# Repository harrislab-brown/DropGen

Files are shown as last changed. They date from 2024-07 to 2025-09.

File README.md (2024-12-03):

## Welcome to DropGen! A droplet on demand generator for research applications developed in the Harris Lab at Brown University

<p align="center">
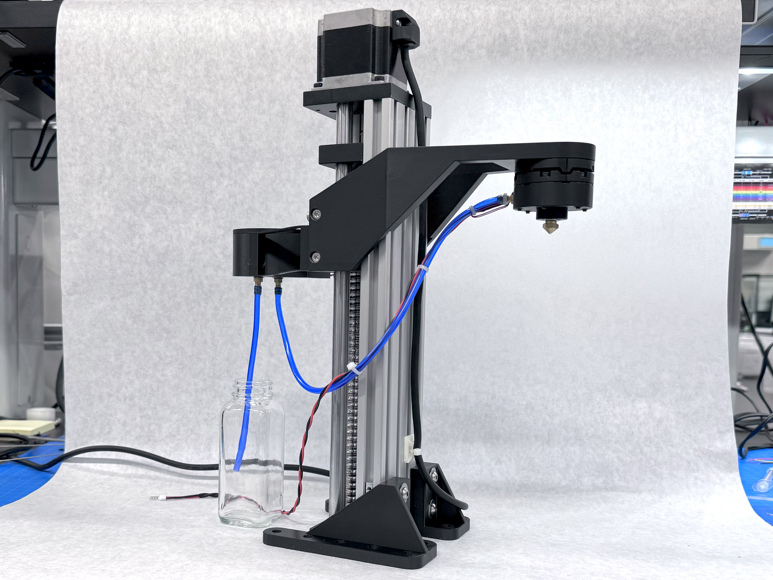
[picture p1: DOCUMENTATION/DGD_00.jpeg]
  
</p>

DropGen uses a fluid reservoir and a piezoelectric buzzer to precisely and repeatably dispense small droplets on demand. 
This new version of the Harris Lab DropGen is designed to be 3D printed using filament based FDM printers. Harris Lab has developed a custom printed circuit board to make assembly and use of DropGen as easy as possible, including adding the ability to control the height of DropGen with a commonly available stepper motor driven linear actuator. 

### WIKI:
Complete build documentation and user guide for DropGen can be found under the [Wiki](https://github.com/harrislab-brown/Filament_DropGen/wiki) tab of this repository.

### CAD: 
The CAD directory contains design files for the droplet generator 3D printed parts and the custom PCB. 
Cad files are available as a .f3z Fusion360 archive file, as well as program agnostic .step files for modification in parametric cad software. All parts that require 3D printing are also available in .stl format which can be used with all modern 3D printing slicers. 

The DropGenPCB directory contains project files for the printed circuit board. The PCB was designed using KiCad 8. Production files ready to send to JLCPCB are available here as well (see wiki for details). 

### CODE: 
DropGen is controlled by a web based GUI running on an ESP32-S3 development board. The wiki contains instructions on how to set up the environment required to flash the ESP32 firmware. 

### Documentation: 
This directory contains image and video assets used in the wiki. 

### Credit: 
If you use or adapt the device for academic publication, please cite this repository as well as the preceding works:
* N. Ionkin and D. M. Harris.  Note: A versatile 3D-printed droplet-on-demand generator. Review of Scientific Instruments. 2018; 89 (11) : 116103. [doi.org/10.1063/1.5054400](doi.org/10.1063/1.5054400)
* D. M. Harris, T. Liu and J. W. M. Bush. A low-cost, precise piezoelectric droplet-on-demand generator. Experiments in Fluids. 2015; 56 (4). [dx.doi.org/10.1007/s00348-015-1950-6](dx.doi.org/10.1007/s00348-015-1950-6)

Happy building!

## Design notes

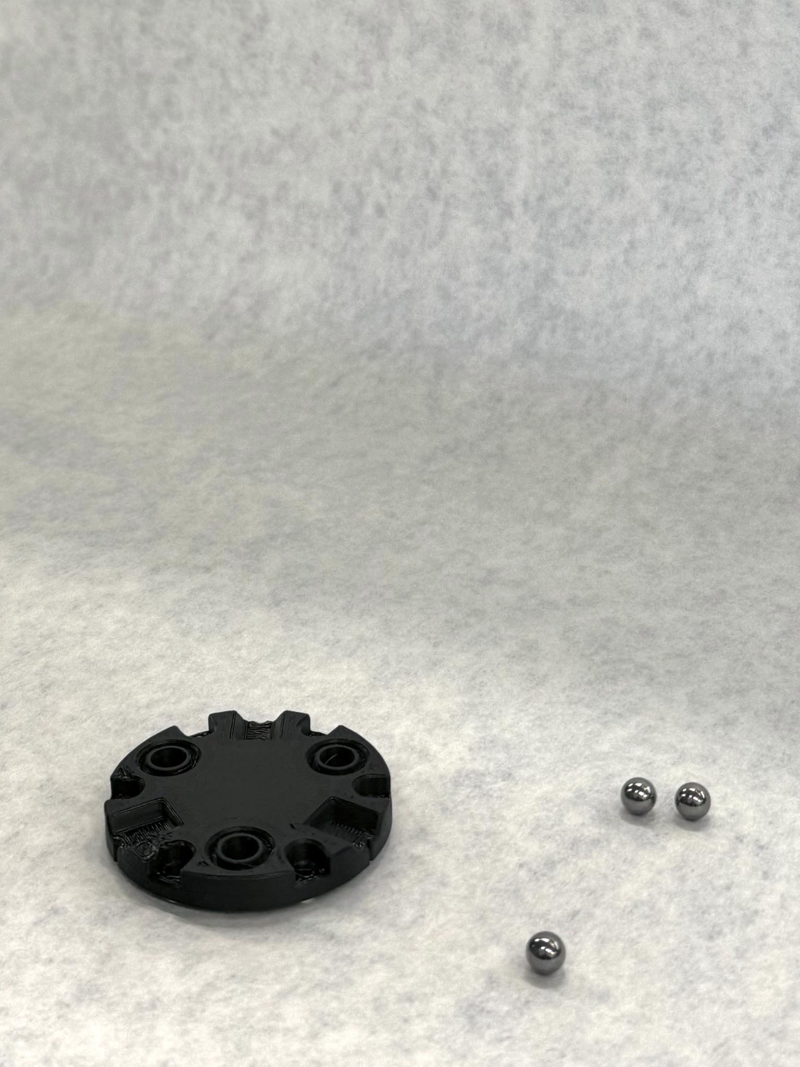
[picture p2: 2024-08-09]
DOCUMENTATION/DGD_15.jpg

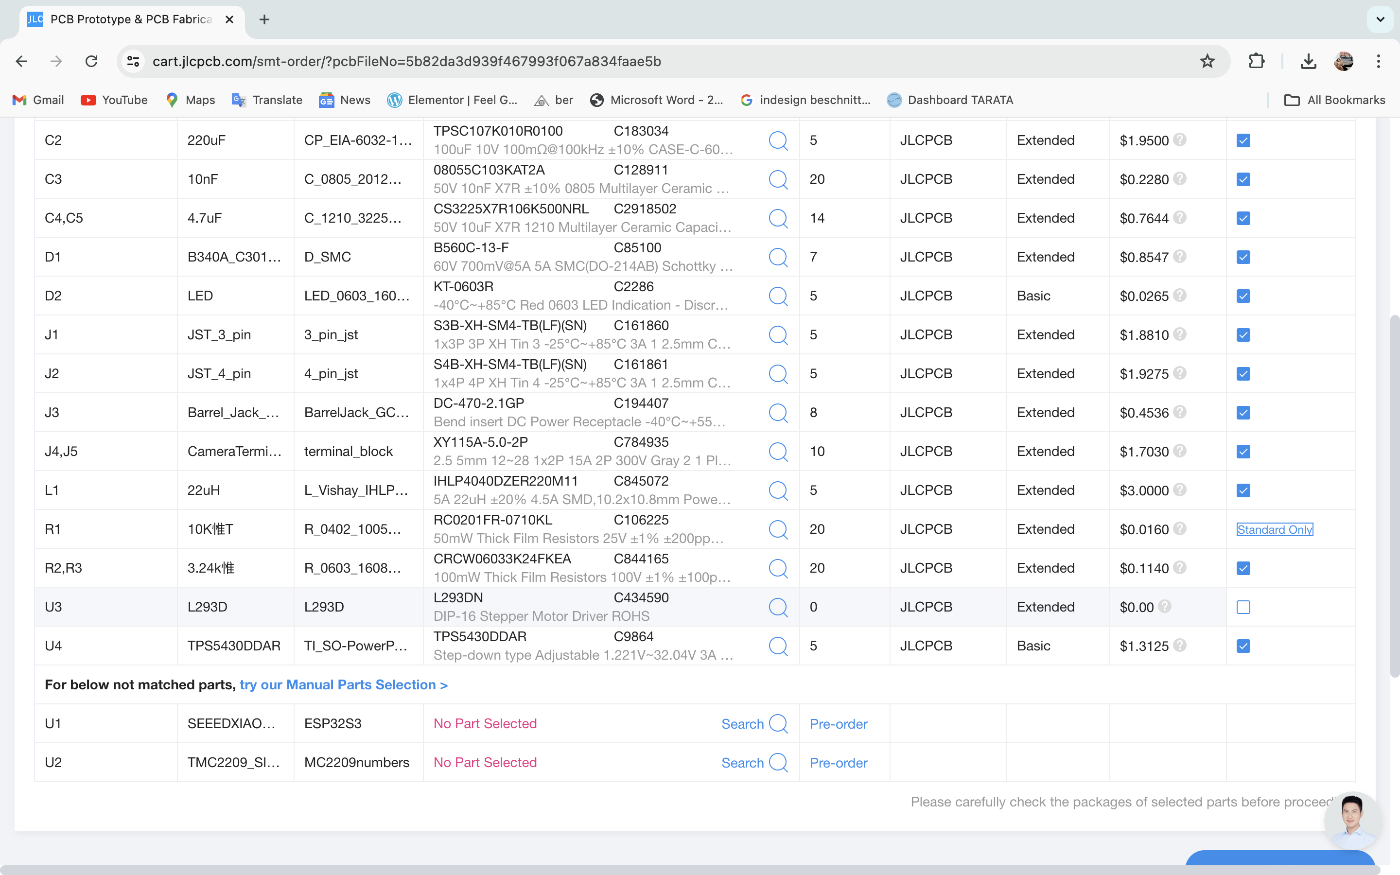
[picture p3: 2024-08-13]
DOCUMENTATION/DGD_83.png

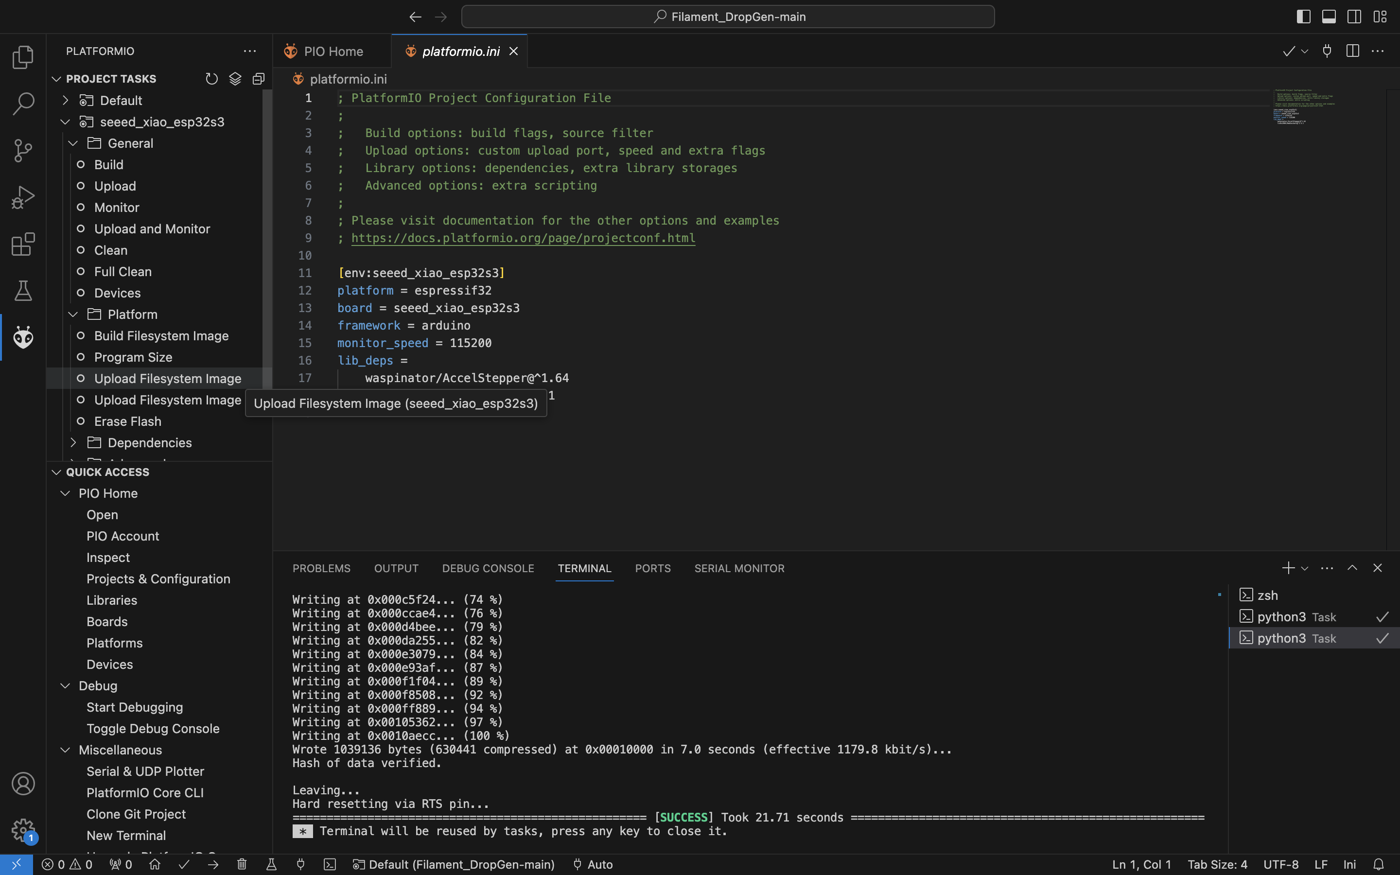
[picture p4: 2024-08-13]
DOCUMENTATION/DGD_91.png

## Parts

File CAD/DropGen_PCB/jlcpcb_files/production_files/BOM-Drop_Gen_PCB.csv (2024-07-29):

Comment | Designator | Footprint | LCSC
10KΩ T | R1 | Resistor_SMD:R_0402_1005Metric | C258091
10nF | C3 | C_0805_2012Metric | C128911
JST_3_pin | J1 | 3_pin_jst | C161860
JST_4_pin | J2 | 4_pin_jst | C161861
220uF | C2 | CP_EIA-6032-15_Kemet-U | C183034
Barrel_Jack_Switch | J3 | BarrelJack_GCT_DCJ200-10-A_Horizontal | C194407
LED | D2 | LED_0603_1608Metric | C2286
4.7uF | C4,C5 | C_1210_3225Metric | C2918502
L293D | U3 | L293D | C434590
100uF | C1 | C_Elec_6.3x7.7 | C72478
Camera Terminal Block | J4,J5 | terminal_block | C784935
3.24kΩ | R2,R3 | R_0603_1608Metric | C844165
22uH | L1 | L_Vishay_IHLP-4040 | C845072
B340A_C3018525 | D1 | D_SMC | C85100
TPS5430DDAR | U4 | TI_SO-PowerPAD-8_ThermalVias | C9864
SEEED XIAO ESP32S3 | U1 | ESP32S3
TMC2209_SILENTSTEPSTICK | U2 | MC2209 numbers

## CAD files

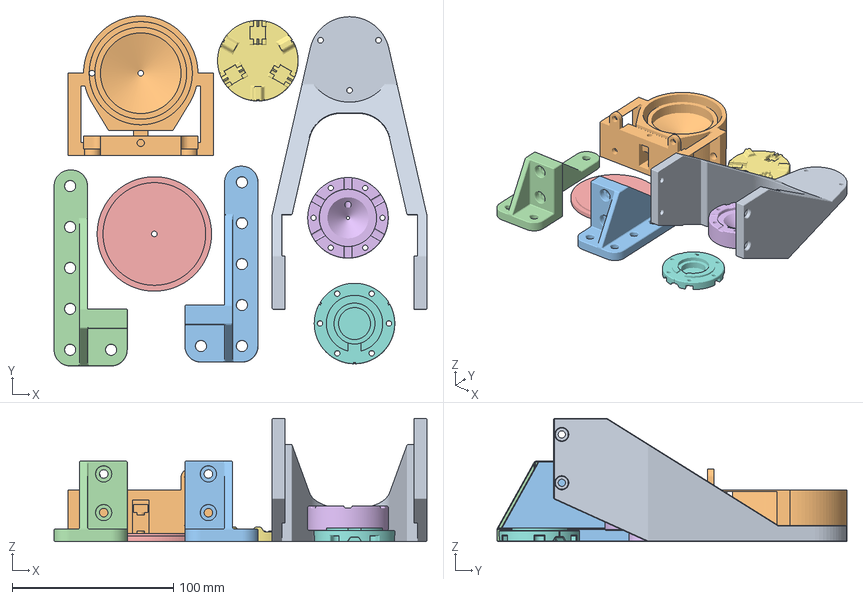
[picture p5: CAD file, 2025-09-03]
CAD/3D_Print_Files/dropgen_full_print_BambuStudio.3mf
231.3 x 217.1 x 76.5 mm
dropgen mount bracket.stl
reservoir.stl
actuator support right.stl
actuator support left.stl
reservoir lid.stl
dropgen lower print.stl
dropgen mount print.stl
dropgen upper print.stl

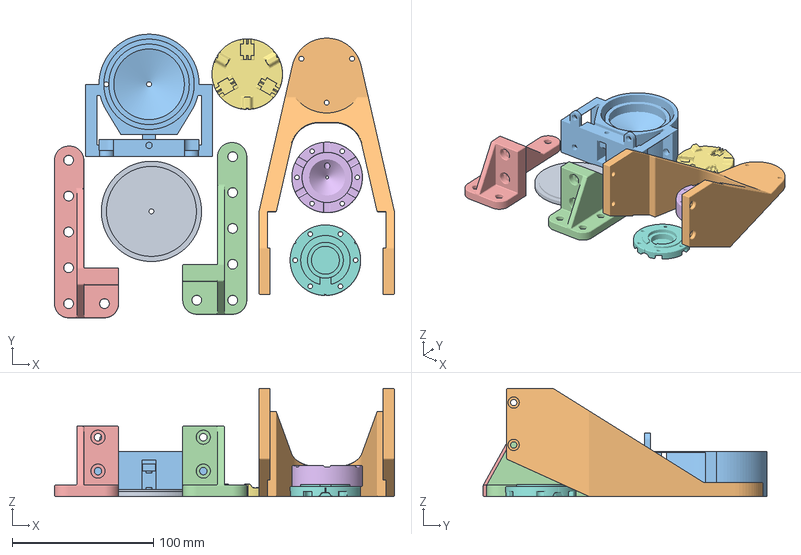
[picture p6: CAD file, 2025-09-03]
CAD/3D_Print_Files/dropgen_full_print_PrusaSlicer.3mf
240.8 x 200.9 x 76.5 mm
dropgen_print_1
dropgen_print_2
dropgen_print_3
dropgen_print_4
dropgen_print_7
dropgen lower print.stl
dropgen mount print.stl
dropgen upper print.stl

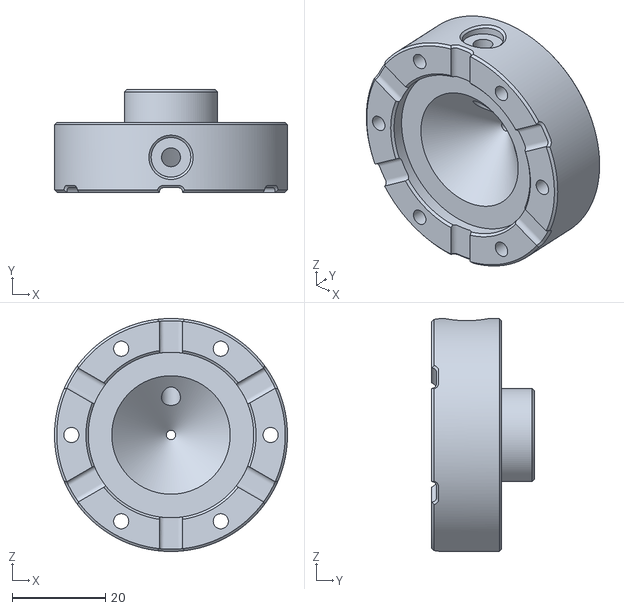
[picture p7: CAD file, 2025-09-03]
CAD/3D_Print_Files/dropgen lower print.stl
50.0 x 22.0 x 50.0

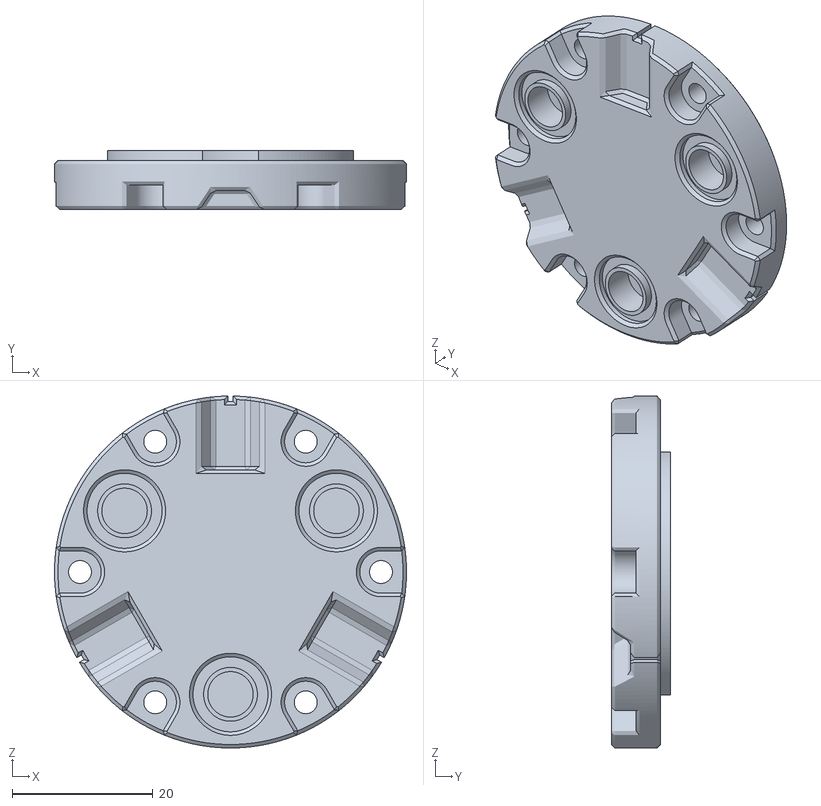
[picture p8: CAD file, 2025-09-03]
CAD/3D_Print_Files/dropgen upper print.stl
50.0 x 8.45 x 50.0

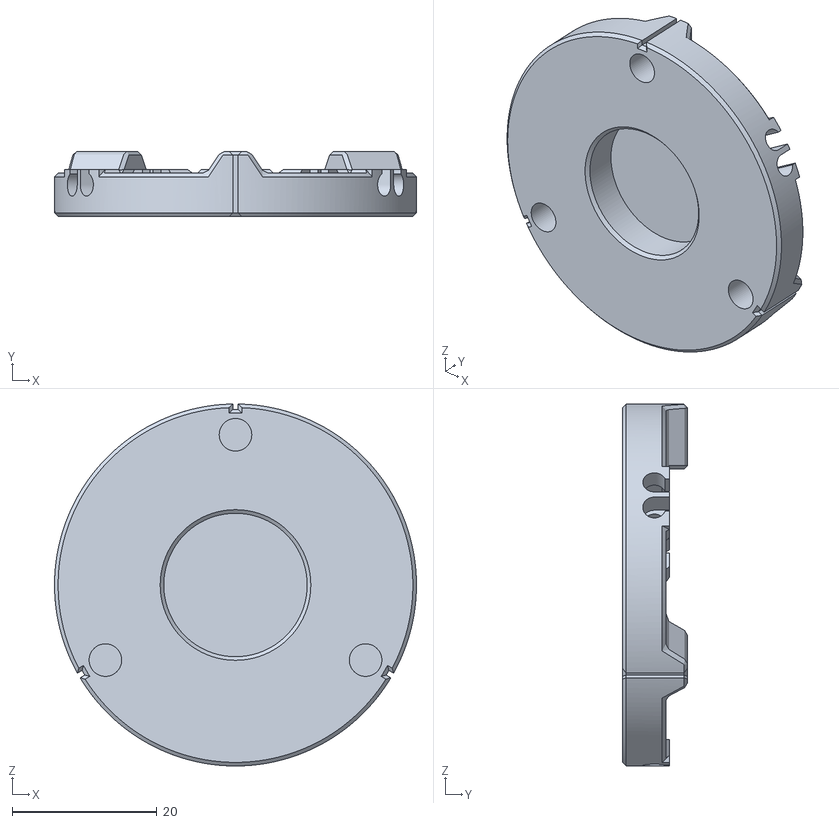
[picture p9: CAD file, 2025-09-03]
CAD/3D_Print_Files/dropgen mount print.stl
50.0 x 9.00 x 50.0

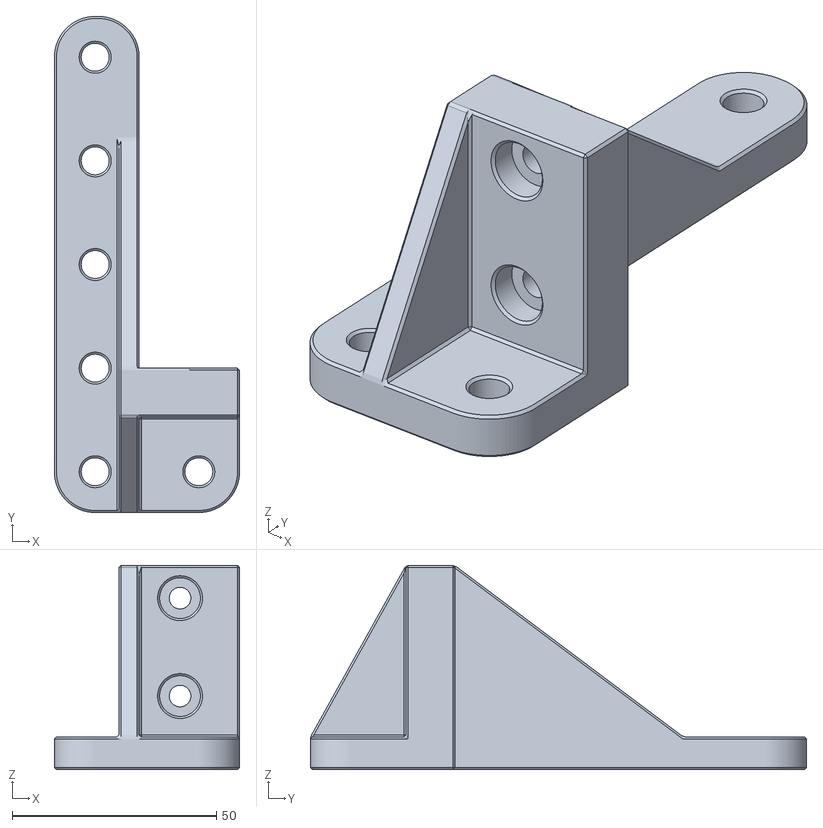
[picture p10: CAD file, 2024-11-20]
CAD/3D_Print_Files/actuator_support_left.stl
45.4 x 121.6 x 50.0

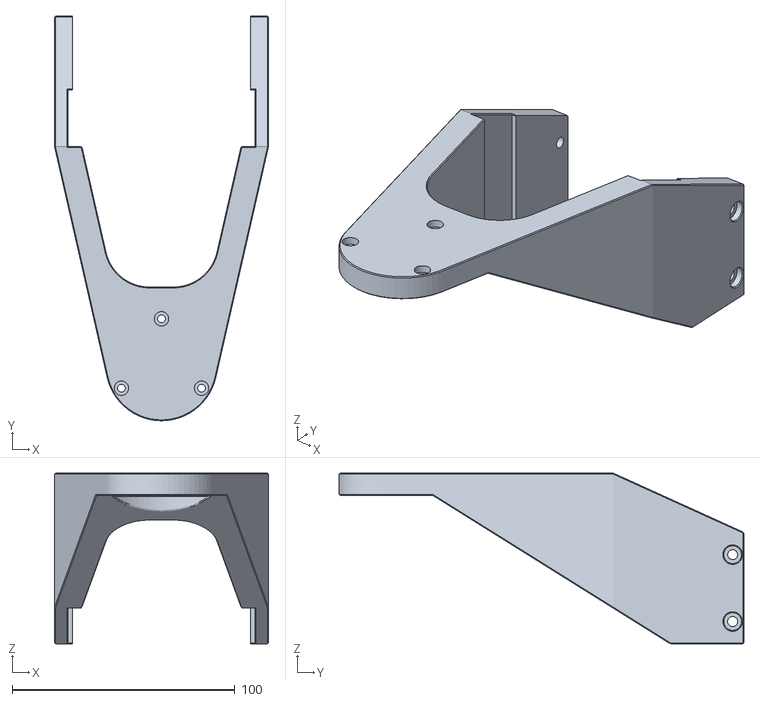
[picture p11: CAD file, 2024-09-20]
CAD/3D_Print_Files/dropgen_mount_bracket.stl
96.0 x 181.5 x 76.5

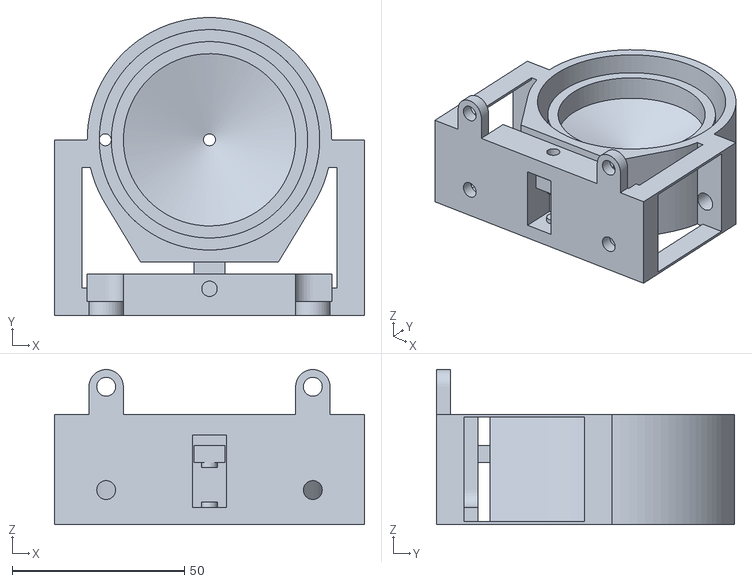
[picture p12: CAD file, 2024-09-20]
CAD/3D_Print_Files/reservoir.stl
90.0 x 86.5 x 45.0

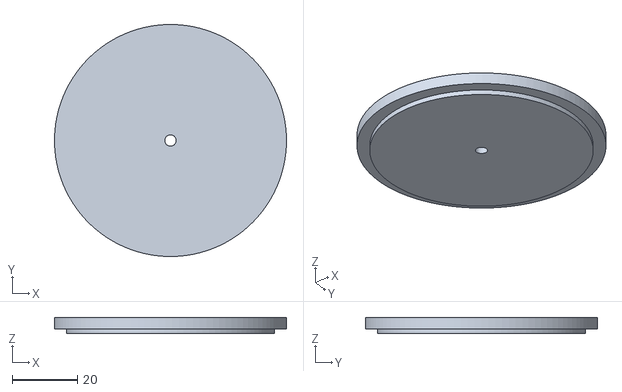
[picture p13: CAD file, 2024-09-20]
CAD/3D_Print_Files/reservoir_lid.stl
71.0 x 71.0 x 5.00

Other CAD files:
CAD/3D_Print_Files/actuator_support_right.stl

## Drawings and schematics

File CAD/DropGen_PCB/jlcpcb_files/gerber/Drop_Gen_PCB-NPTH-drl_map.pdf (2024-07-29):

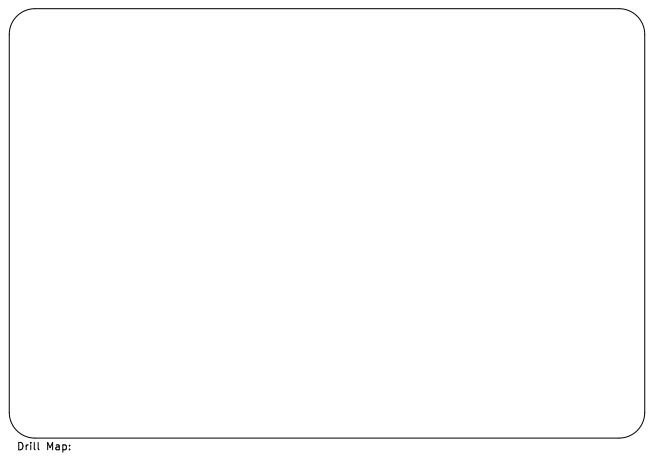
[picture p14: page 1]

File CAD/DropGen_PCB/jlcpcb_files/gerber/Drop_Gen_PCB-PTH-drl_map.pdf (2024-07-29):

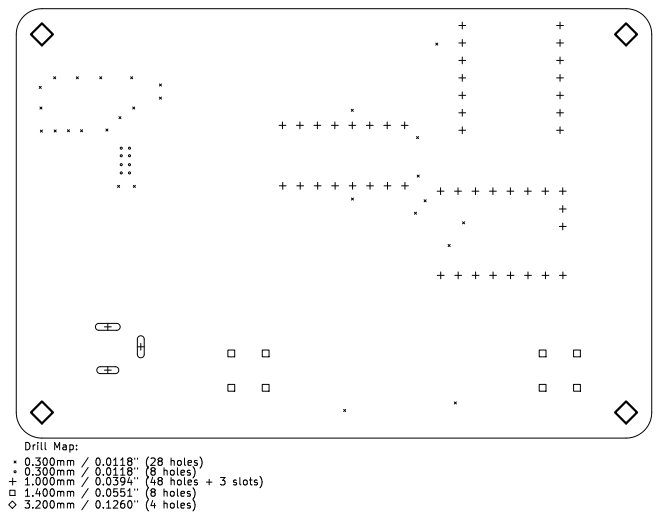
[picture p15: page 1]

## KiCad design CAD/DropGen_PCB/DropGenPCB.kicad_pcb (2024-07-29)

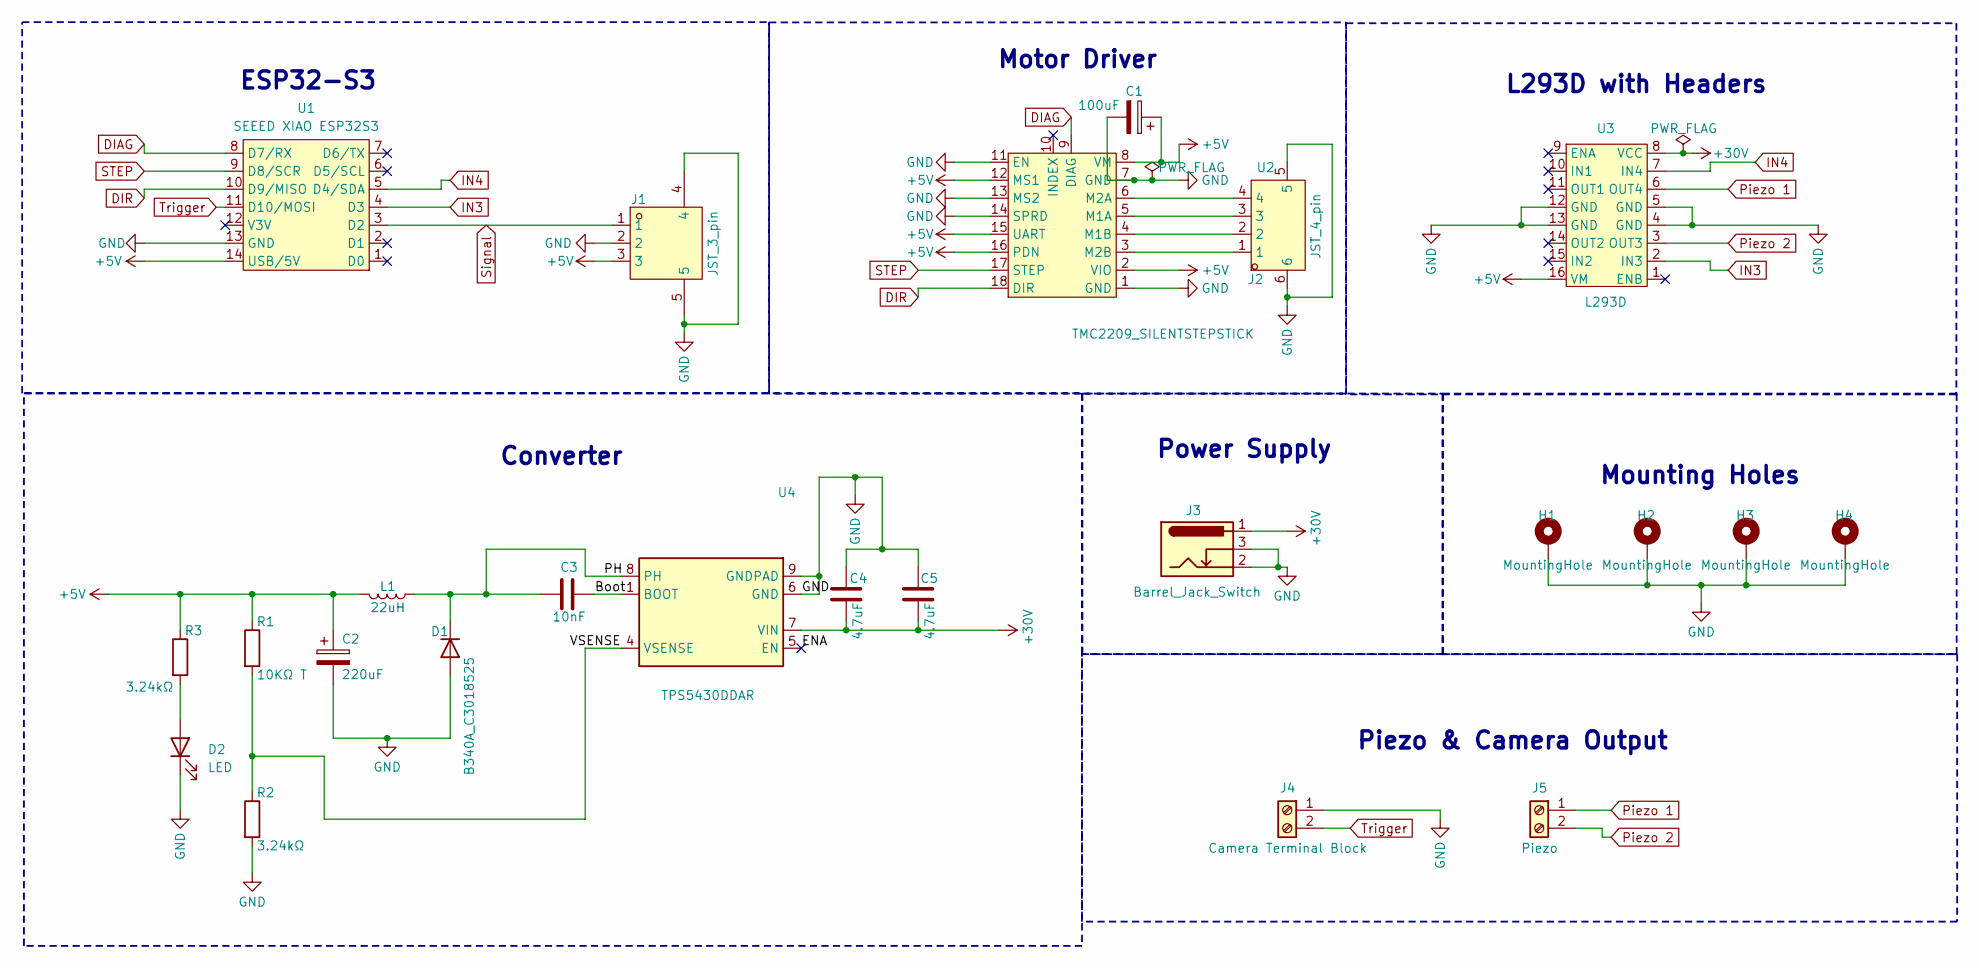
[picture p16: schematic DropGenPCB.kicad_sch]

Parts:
C1: 100uF; C_Elec_6.3x7.7; Manufac. Part RVT1V101M0607; LCSC C72478
C2: 220uF; CP_EIA-6032-15_Kemet-U; Manufac. Part TPSC107K010R0100; LCSC C183034
C3: 10nF; C_0805_2012Metric; Manufac. Part 08055C103KAT2A; LCSC C128911
C4, C5: 4.7uF; C_1210_3225Metric; Manufac. Part CS3225X7R106K500NRL; LCSC C2918502
D1: B340A_C3018525; D_SMC; Manufac. Part B560C-13-F; LCSC C85100
D2: LED; LED_0603_1608Metric; Manufac. Part KT-0603R; LCSC C2286
H1, H2, H3, H4: MountingHole; MountingHole_3.2mm_M3_DIN965_Pad
J1: JST_3_pin; 3_pin_jst; Manufac. Part S3B-XH-SM4-TB(LF)(SN); LCSC C161860
J2: JST_4_pin; 4_pin_jst; Manufac. Part S4B-XH-SM4-TB(LF)(SN); LCSC C161861
J3: Barrel_Jack_Switch; BarrelJack_GCT_DCJ200-10-A_Horizontal; Manufac. Part DC-470-2.1GP; LCSC C194407
J4: Camera Terminal Block; terminal_block; Manufac. Part XY115A-5.0-2P; LCSC C784935
J5: Piezo; terminal_block; Manufac. Part XY115A-5.0-2P; LCSC C784935
L1: 22uH; L_Vishay_IHLP-4040; Manufac. Part IHLP4040DZER220M11; LCSC C845072
R1: 10KΩ T; R_0402_1005Metric_Pad0.72x0.64mm_HandSolder; Manufac. Part RC0201FR-0710KL; LCSC C25744
R2, R3: 3.24kΩ; R_0603_1608Metric; Manufac. Part CRCW06033K24FKEA; LCSC C844165
U1: SEEED XIAO ESP32S3; ESP32S3; Manufac. Part 113991114
U2: TMC2209_SILENTSTEPSTICK; MC2209 numbers; Manufac. Part 787794452214
U3: L293D; Manufac. Part L293DN; LCSC C434590
U4: TPS5430DDAR; TI_SO-PowerPAD-8_ThermalVias; Manufac. Part TPS5430DDAR; LCSC C9864

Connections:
+5V: C1.1, C2.1, J1.3, L1.2, R1.1, R3.1, U1.14 (USB/5V), U2.2 (VIO), U2.8 (VM), U2.12 (MS1), U2.15 (UART), U2.16 (PDN), U3.16 (VM)
+30V: C4.2, C5.2, J3.1, U3.8 (VCC), U4.7 (VIN)
/Boot: C3.2, U4.1 (BOOT)
/ENA: U4.5 (EN)
/PH: C3.1, D1.1 (K), L1.1, U4.8 (PH)
/VSENSE: R1.2, R2.1, U4.4 (VSENSE)
DIAG: U1.8 (D7/RX), U2.9 (DIAG)
DIR: U1.10 (D9/MISO), U2.18 (DIR)
GND: C1.2, C2.2, C4.1, C5.1, D1.2 (A), D2.1 (K), H1.1, H2.1, H3.1, H4.1, J1.2, J1.4, J1.5, J2.5, J2.6, J3.2, J3.3, J4.1, R2.2, U1.13 (GND), U2.1 (GND), U2.7 (GND), U2.11 (EN), U2.13 (MS2), U2.14 (SPRD), U3.4 (GND), U3.5 (GND), U3.12 (GND), U3.13 (GND), U4.6 (GND), U4.9 (GNDPAD)
IN3: U1.4 (D3), U3.2 (IN3)
IN4: U1.5 (D4/SDA), U3.7 (IN4)
unnamed: D2.2 (A), R3.2
unnamed: J2.3, U2.5 (M1A)
unnamed: J2.2, U2.4 (M1B)
unnamed: J2.4, U2.6 (M2A)
unnamed: J2.1, U2.3 (M2B)
Piezo 1: J5.1, U3.6 (OUT4)
Piezo 2: J5.2, U3.3 (OUT3)
STEP: U1.9 (D8/SCR), U2.17 (STEP)
Signal: J1.1, U1.3 (D2)
Trigger: J4.2, U1.11 (D10/MOSI)

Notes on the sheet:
Mounting Holes
ESP32-S3
Converter
Motor Driver
Piezo & Camera Output
L293D with Headers
Power Supply

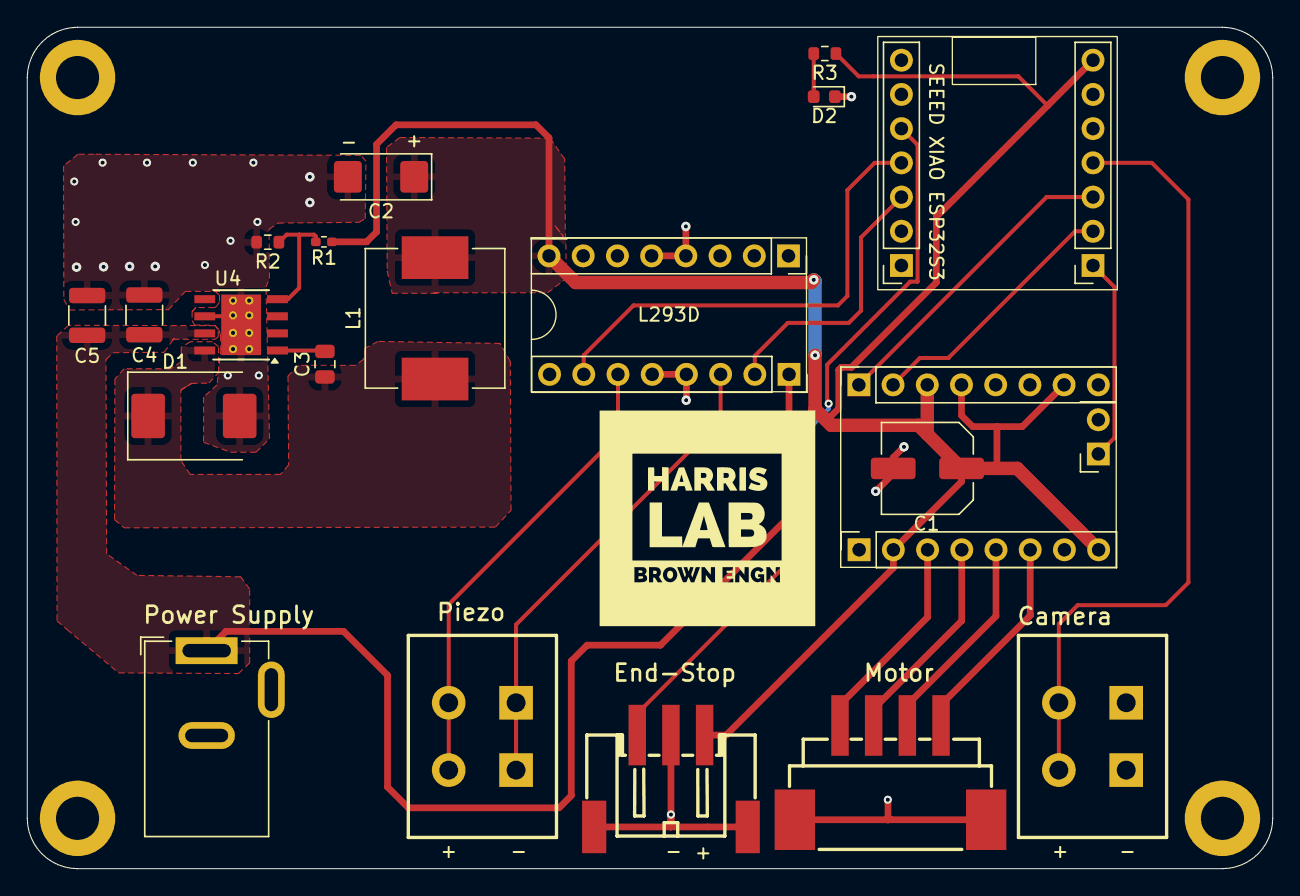
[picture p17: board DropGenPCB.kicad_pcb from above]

Board: 2 copper layers, 92.5 x 62.5 mm, 24 parts (0 on the bottom side), 20 nets.

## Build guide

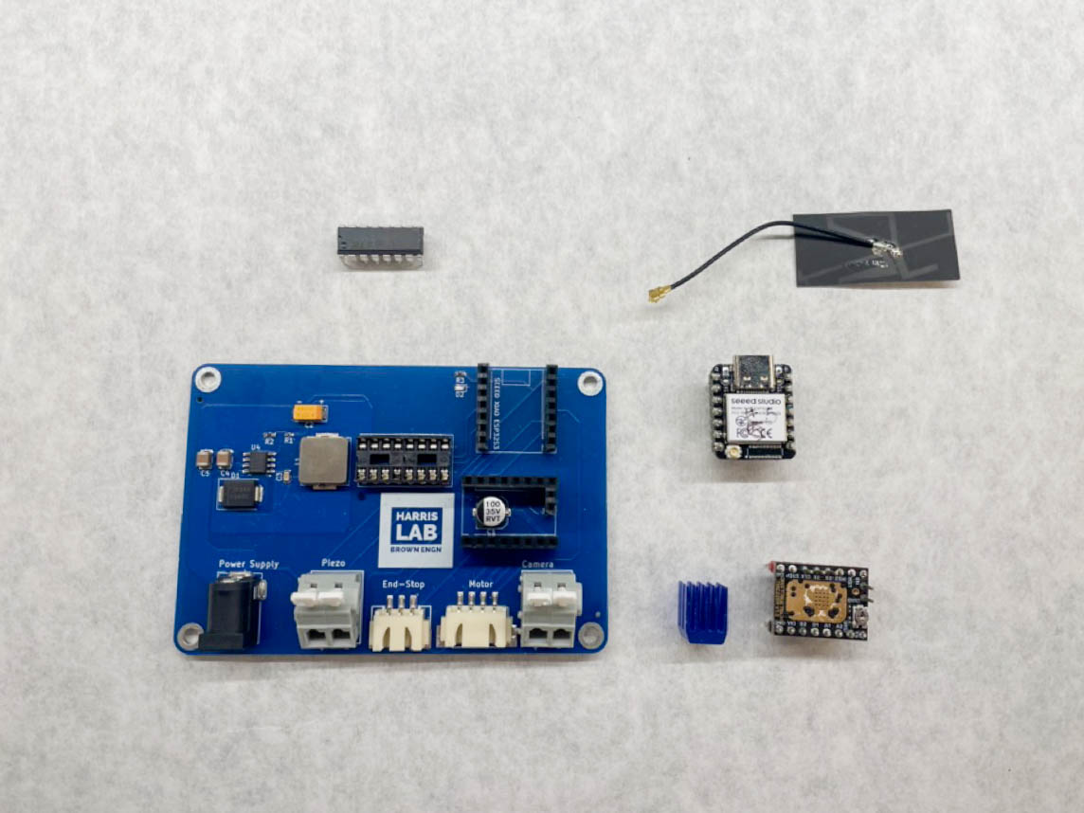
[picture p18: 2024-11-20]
DOCUMENTATION/pcb_assembly-3.jpg

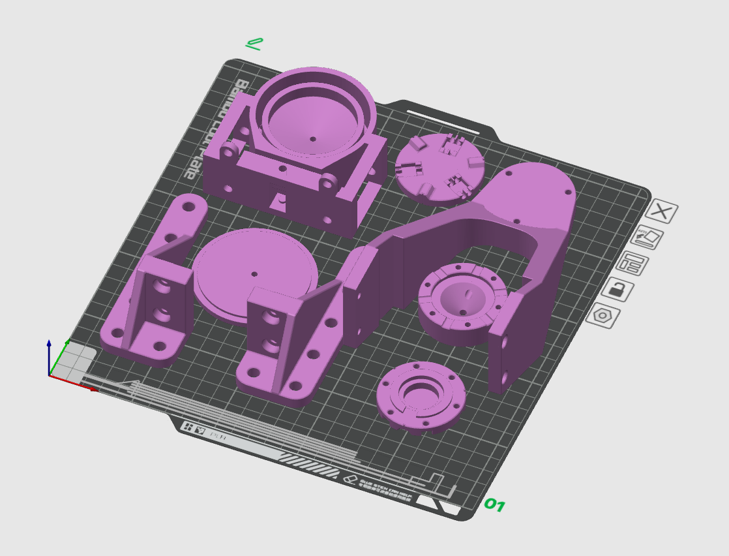
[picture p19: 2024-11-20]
DOCUMENTATION/3D_print_orientation.png

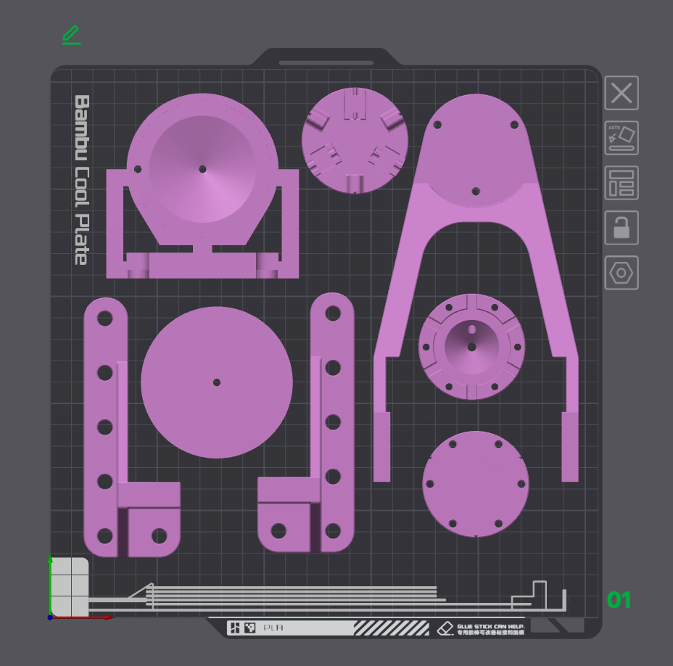
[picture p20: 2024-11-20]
DOCUMENTATION/3D_print_layout.png

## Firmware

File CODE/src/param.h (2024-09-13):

#ifndef PARAM_H
#define PARAM_H
#include <Preferences.h>

struct Param {

  public:
    
    // Wifi definitions.
    const bool WIFI_STATION = true;    // True for external WiFi connection
    const char* SSID        = "YOUR_NETWORK_NAME";
    const char* PASSWORD    = "YOUR_NETWORK_PASSWORD";
    const char* DNS_NAME    = "dropgen";
    
    // Drop generator pin definitions
    const int DIR_A      = 5;          // Piezo PWN pin 1
    const int DIR_B      = 4;          // Piezo PWN pin 2
    const int TRIG       = 9;          // Camera trigger
    const int LED        = 21;         // BUILTIN_LED

    // Motor pin definitions
    // const int RES_DIAG    = 9;         // Reservoir motor diagnostic pin
    const int RES_STEP    = 7;         // Reservoir motor step pin
    const int RES_DIR     = 8;         // Reservoir motor direction pin
    const int RES_ENDSTOP = 3;         // Reservoir mechanical end stop pin

    // Drop generator parameters
    int pulseWidth       = 1000;       // Piezo pulse width in microseconds
    int dropDelay        = 500;        // Time between droplets in milliseconds
    int dropNum          = 100;        // Number of droplets
    int cameraDelay        = 15;         // Camera delay from drop pulse end in milliseconds
    volatile bool camera = false;      // Camera on/off
    volatile bool drop   = false;      // Droplet generator on/off
    
    // Motor variables
    bool calibrate       = false;      // Calibrate the motors
    double resMotPos     = 0.0;        // Reservoir motor position
    double travelLength  = 1;          // Motor travel length (mm)
    int SPEED            = 5000;       // Motor speed
    int CALIB_SPEED      = 2000;       // Calibration Motor speed
    int ACCEL            = 4000;       // Motor acceleration
    int LEAD_SIZE        = 1280;       // Motor round size (steps / mm)

    void loadParameters(Preferences &pref){
      pulseWidth       = pref.getInt("PW", pulseWidth);
      dropDelay        = pref.getInt("DD", dropDelay);
      dropNum          = pref.getInt("DN", dropNum);
      travelLength     = pref.getInt("TL", travelLength);
      cameraDelay        = pref.getInt("DT", cameraDelay);
      resMotPos        = pref.getInt("RMP", resMotPos);
    }
};
extern Param param;

#endif

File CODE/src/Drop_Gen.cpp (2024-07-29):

#include <Arduino.h>
#include "Drop_Gen.h"
#include "param.h"

#define PIEZO_A (1 << param.DIR_A)
#define PIEZO_B (1 << param.DIR_B)
#define TRIGGER (1 << param.TRIG)
volatile int *pulsewidth = &param.pulseWidth;

// setup function for L298N H-bridge and camera
void Generator::dgSetup(){
  pinMode(param.LED,      OUTPUT);
  pinMode(param.DIR_A,    OUTPUT);
  pinMode(param.DIR_B,    OUTPUT);
  pinMode(param.TRIG,     OUTPUT);
  digitalWrite(param.LED, HIGH);
}

// piezodisk trigger with camera function
void Generator::dgStart(){
  int drop_index = 0;
  while(drop_index < param.dropNum && param.drop){
    Serial.println(*pulsewidth);
    noInterrupts();
    generate();
    interrupts();
    drop_index ++;

    int delayTime = param.dropDelay;
    if(param.camera){
     camera();
     delayTime -= param.cameraDelay;
    }
    delay(delayTime);
    
  }
  param.drop = false;

  // if(param.drop){
  //   Serial.println(*pulsewidth);
  //   noInterrupts();
  //   generate();
  //   interrupts();
  //   if(param.camera) camera();
  // }
}

void Generator::camera(){
  delay(param.cameraDelay);
  GPIO.out_w1ts = TRIGGER;
  delayMicroseconds(50);
  GPIO.out_w1tc = TRIGGER;
}


void IRAM_ATTR Generator::generate(){
  GPIO.out_w1ts = PIEZO_A;  // Turn on left: HIGH
  GPIO.out_w1tc = PIEZO_B;  // Turn off right: LOW
  delayMicroseconds(*pulsewidth);  // Pulse width
  GPIO.out_w1tc = PIEZO_A;  // Turn off left: LOW
  GPIO.out_w1ts = PIEZO_B;  // Turn on right: HIGH
}

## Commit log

2024-07-25 changed how motor run command is called
2024-07-31 fixed camera triggering (wrong pin map)
2024-09-05 changed repository file structure
    [BOM-Drop_Gen_PCB.csv, CPL-Drop_Gen_PCB.csv, DropGenPCB.kicad_pcb, DropGenPCB.kicad_sch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]
2024-11-20 changed folder naming, added 3d print screenshots
    [BOM-Drop_Gen_PCB.csv, CPL-Drop_Gen_PCB.csv, DropGenPCB.kicad_pcb, DropGenPCB.kicad_sch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]
2024-11-20 added pcb and endstop photos
2025-09-03 updated cad files with M6 revision
    [dropgen lower print.stl, dropgen mount print.stl, dropgen upper print.stl, dropgen_assembly.f3z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]
